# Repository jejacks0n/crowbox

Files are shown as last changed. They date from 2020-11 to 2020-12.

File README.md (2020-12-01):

CrowBox (UNOFFICIAL REPO)
=========================

This is an unofficial repository of resources for the [CrowBox project](http://www.thecrowbox.com). IT IS NOT OFFICIAL, and reflects only the changes I've made. If you want, check out the `original` branch for the original resources as they were when this repo was created.

## About the Project

The CrowBox is an experimentation platform designed to autonomously train corvids (the family of birds crows belong to). So far we’ve trained captive crows to deposit dropped coins they found on the ground in exchange for peanuts. The next step is to work with wild corvids and see if we can get them to learn to use the box, then to optimize the training protocol to see how quickly they can learn from each other.

That's where you come in. Different corvids learn at different speeds and in different ways, and the only way to figure out the best way to teach them is through experimentation. The more people try different things the faster we'll all figure out how to work cooperatively with crows.

Once we’ve got the system optimized for teaching coin collection we can move to seeing how flexibly they can learn *other* tasks, like collecting garbage, sorting through discarded electronics, or maybe even search and rescue.

The idea isn't to get rich off found coins - we want to change the world through learning how to cooperate with other species.

## How it Works

Based on established Skinnerian training principles, the action of the device is divided into four stages:

- Stage 1: Discovery and free feeding
- Stage 2: Food available on landing
- Stage 3: Food available on coin deposit, training coins provided
- Stage 4: Food available on coin deposit

So far the CrowBox project has been shown to work with captive crows. Now we're releasing the open sourced designs of the new CrowBox so anyone can try it with their own wild corvid populations!

## Project Objectives

Nobody's going to get rich training corvids, but we might just change how humanity engages with other species.

The CrowBox is an appliance for experimentation in training and interacting with these birds: it's our goal to get people to think differently about how humanity is already training animals like crows, rats, racoons, deer, and other animals that live near us.

Right now we're teaching them to survive as parasites; what would happen if we could find mutually beneficial working relationships instead?

#### As Seen on TED

Watch the [TED Talk](https://www.ted.com/talks/joshua_klein_a_thought_experiment_on_the_intelligence_of_crows).

"Hacker and author [Joshua Klein](https://www.josh.is) is fascinated by crows. After a long amateur study of corvid behavior, he's come up with an elegant machine that may form a new bond between animal and human."

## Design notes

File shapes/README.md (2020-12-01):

CrowBox Shape Files
===================

The SVG shape files here are intended to be used with a laser cutting provider like [Ponoko](https://www.ponoko.com) or to be laser cut at a local maker shop or similar. They're designed to be cut on sheets of 790mm x 384mm (31.1” x 15.1”) acrylic with a thickness of 3mm, and .5mm styrene.

Once you have the housing parts, check out our YouTube Channel for step-by-step assembly videos.

## Ponoku Specific Instructions

You should only need to upload three files total. The transparent acrylic shapes comes in a single or double layout. You can use the double layout to order two sheets of color acrylic and a single sheet of transparent acrylic to build two boxes.

- [color acrylic](https://raw.githubusercontent.com/jejacks0n/crowbox/shapes-3.0/shapes/crowbox_v3_r1_color_acrylic.svg)
- [transparent acrylic (single layout)](https://raw.githubusercontent.com/jejacks0n/crowbox/shapes-3.0/shapes/crowbox_v3_r1_transparent_acrylic_single.svg) or [(double layout)](https://raw.githubusercontent.com/jejacks0n/crowbox/shapes-3.0/shapes/crowbox_v3_r1_transparent_acrylic_double.svg)
- [styrene](https://raw.githubusercontent.com/jejacks0n/crowbox/shapes-3.0/shapes/crowbox_v3_r1_styrene.svg)

<small>Right click links and "Save as..." to download.</small>

When you select the designs and add them to your cart, you're welcome to select whichever color acrylic you'd like. Some of the matte finishes are nice, and it's important to understand and consider that color may play a role in the success of your CrowBox deployment, as crows (and other birds) have unique color vision.

- [Article: Birds Can See a 'Colour' Humans Can't. Now Scientists Have Revealed This Hidden World](https://www.sciencealert.com/birds-can-see-uv-light-now-scientists-can-show-us-what-that-looks-like)
- [Article: Crows remember colours for a year: Japanese study](https://phys.org/news/2011-12-crows-colours-year-japanese.html)
- [Article: Can't crows see yellow?](http://www.gaiapress.com/en/article/525.html)

Note that Ponoko shipping charges make up a big chunk of the final cost of a single set of parts - it's much more price-effective if you and a friend order your sets of parts together. Huge thanks to Danita Craft for pulling these together; see [this thread](https://groups.google.com/g/crowboxkit/c/9xb9-OHnaKQ/m/a6WmhurxAQAJ?pli=1) for more info.

**Disclaimer:** _We have bought several sets of CrowBox parts from Ponoko in order to verify their quality and accuracy. We have had good customer service experiences with them, as well. For these reasons, we're happy to recommend Ponoko as a place for you to buy your parts. Ponoko charges fees for materials, manufacturing services, and shipping but we have no financial interest or affiliation with them. We receive no money when parts are bought at Ponoko - we're just making a service recommendation._

If you'd like to consider other online laser-cutting services, you can download the housing geometry source files from here and submit them to a service of your choosing.

## Source File

The source `.afdesign` file is provided to make refinements or adjustments of your own easier. The source file has been generated using [Affinity Designer](https://affinity.serif.com/en-us/designer), which is a great application and available for a 7 day trial. The trial may be long enough for you to make the desired changes and export new SVG files. The provided SVG files are optimized to reduce multiple passes on laser cutting.

When you export SVGs it's recommended to run them through [ImageOptim](https://imageoptim.com/mac), which helps clean up a lot of things, especially some pesky width/height attributes that can confuse Ponoko or other laser cutters.

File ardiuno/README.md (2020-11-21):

CrowBox Software (CrOS)
=======================

The programmable computer brain that controls the CrowBox is the Arduino UNO microcontroller board.

We'll go through the steps to download the source code for the CrOS software and get it uploaded to an Arduino UNO board, which can then be used to control your CrowBox.

The CrOS software is fully open-source and we encourage you to make changes and improvements to the code and the machine's training protocol.

The Arduino is an extremely popular platform for makers and experimental electronics worldwide. This means that there are a great deal of resources available to help you learn more about the Arduino hardware, the Arduino IDE software, and how to program and modify programs for these great little boards.

If you run into trouble following the instructions on this page, feel free to open an issue, or check out one of these resources for more information:

- [Getting Started with Arduino](https://www.arduino.cc/en/Guide)
- [Arduino UNO Guide](https://www.arduino.cc/en/Guide/ArduinoUno)
- [CrowBox Google Group](http://groups.google.com/group/CrowBoxKit)

### Table of contents

- [Step 1: Download and Install the Arduino IDE Software](#step-1-download-and-install-the-arduino-ide-software)
- [Step 2: Download and Extract the CrOS Software](#step-2-download-and-extract-the-cros-software)
- [Step 3: Load CrOS Software into the Arduino IDE](#step-3-load-cros-software-into-the-arduino-ide)
- [Step 4: Connect the Arduino UNO Board](#step-4-connect-the-arduino-uno-board)
- [Step 5: Upload the CrOS Software to the Arduino UNO Board](#step-5-upload-cros-software-to-arduino-uno-board)

## Step 1: Download and Install the Arduino IDE Software

To install the CrOS Software onto your Arduino UNO microcontroller board, you'll need a computer, a USB (A to B) cable, and the Arduino IDE software, which is available for free download. IDE stands for Integrated Development Environment, but that's not an important detail right now.

Let's get started! First, follow the official instructions at the Arduino website to download and install the version of the Arduino IDE software that matches your computer's operating system:

- [Windows](https://www.arduino.cc/en/Guide/Windows)
- [Mac OSX](https://www.arduino.cc/en/Guide/MacOSX)
- [Linux](https://www.arduino.cc/en/Guide/Linux)

## Step 2: Download and Extract the CrOS Software

In order to get your CrowBox functional, you'll need to download our CrOS software and install it on your Arduino UNO board.

Download the [latest version of the CrOS software].

After you've downloaded this file you should extract the archive, which you can do by double-click the .zip file you've downloaded.

The archive should create a folder named cros which contains the CrOS source code files, which have extensions like .h, .cpp, and a file named cros.ino.

## Step 3: Load CrOS Software into the Arduino IDE

Launch the Arduino IDE software that you downloaded and installed in the previous steps.

From the Arduino menu, select FILE → OPEN. In the file dialog window that appears, navigate to the 'cros_source' folder from step three and select the file named cros.ino then click Open.

The CrOS project files will be loaded and you will see some tabs containing filenames that begin with 'cros'. You can click through these tabs to view the various source code files, or just ignore them if you're not interested.

It's possible that at some point a window will appear near the bottom of the Arduino IDE which says "Updates are available for some of your boards and libraries". It's a good idea to accept these updates, but you may also click the `X` to dismiss this message and ignore the updates.

## Step 4: Connect the Arduino UNO Board

Plug the 'B' end (The big square end) of your USB A to B cable into the square USB socket on your Arduino UNO board. Plug the other end of the USB cable into a free USB port on your computer.

Allow a moment for your operating system to detect the new device. On Windows operating systems, drivers may begin to install. If so, allow this process to finish before proceeding.

In the Arduino IDE menu, select TOOLS → BOARD → ARDUINO/GENUINO UNO.

The details of the next step depend on your operating system:

### Windows

In the Arduino IDE menu, select TOOLS → PORT → and then look for a COM port numbered 3 or higher which is also labeled (Arduino/Genuino Uno) and select it.

Examples: COM6 (Arduino/Genuino Uno) or COM3 (Arduino/Genuino Uno)

### Mac OSX

In the Arduino IDE menu, select TOOLS → PORT → and then select the port named starting with /dev/tty.usbmodem or /dev/tty.usbserial. The port name will probably end with an unusual alphanumeric string.

### Linux

We have no instructions for this step at present! If you are familiar with the Arduino IDE on Linux, please contribute to this section.

## Step 5: Upload CrOS Software to Arduino UNO Board

At the top left of the Arduino IDE window you'll see two round buttons. Locate the round button with an arrow facing to the right. This is the Upload button.

Click the Upload button.

The CrOS software will compile on your computer and then be uploaded to the Arduino UNO board which you've connected to your computer with the USB cable. If you receive an error message, the best place to turn for help is the issues, or the [CrowBox Google Group](http://groups.google.com/group/CrowBoxKit)

Once the upload is complete, leave the Arduino UNO board connected to your computer for 30 seconds before disconnecting the USB cable.

Your CrowBox software should now be ready to operate!

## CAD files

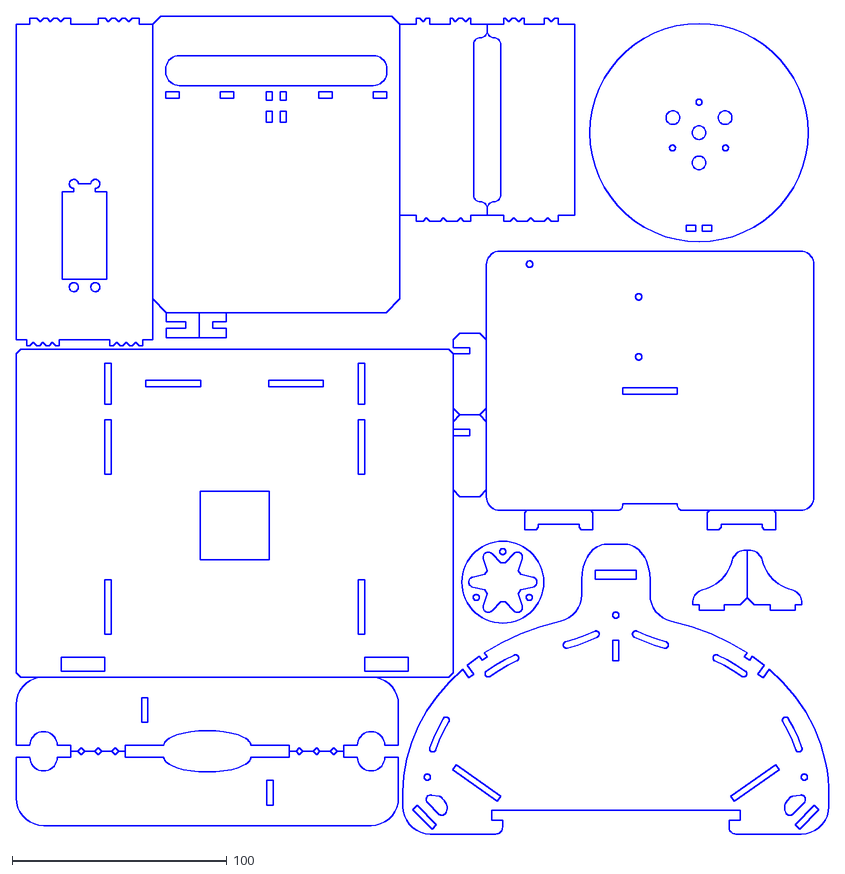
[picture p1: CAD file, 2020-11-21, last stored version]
shapes/crowbox_v2_r2_transparent.dxf
378.0 x 380.6

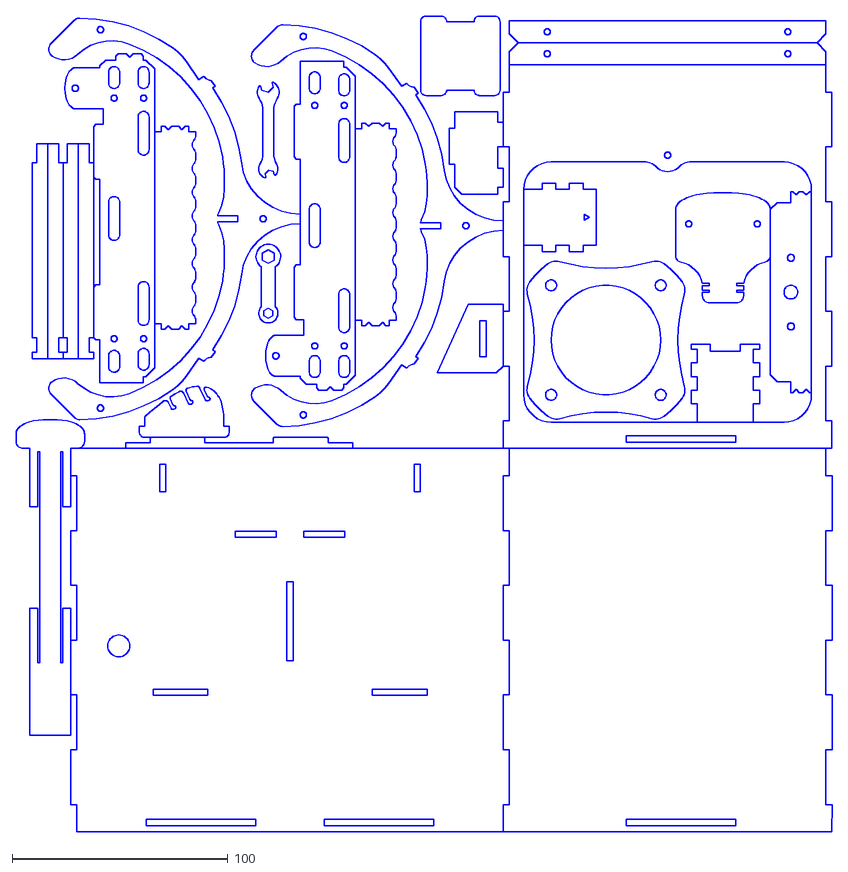
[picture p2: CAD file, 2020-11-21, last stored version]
shapes/source/crowbox_v2_r2_dark.dxf
378.2 x 378.1

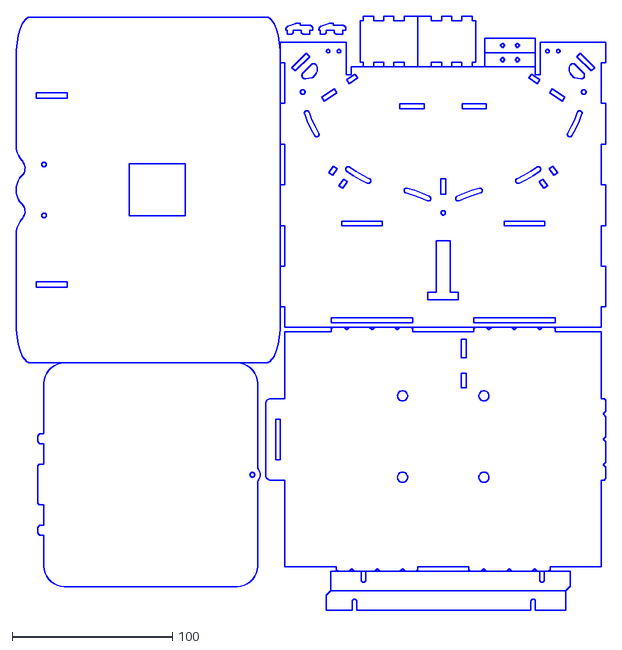
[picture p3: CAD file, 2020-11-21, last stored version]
shapes/crowbox_v2_r2_light.dxf
368.3 x 370.8

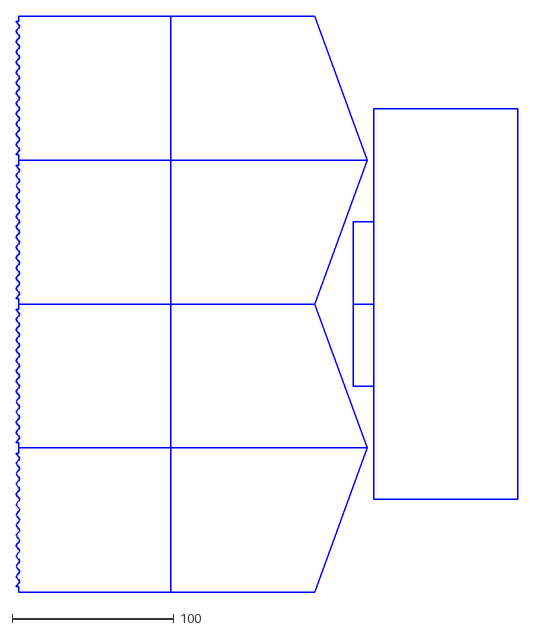
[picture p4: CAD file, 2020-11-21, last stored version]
shapes/crowbox_v2_r2_styrene.dxf
309.7 x 355.6

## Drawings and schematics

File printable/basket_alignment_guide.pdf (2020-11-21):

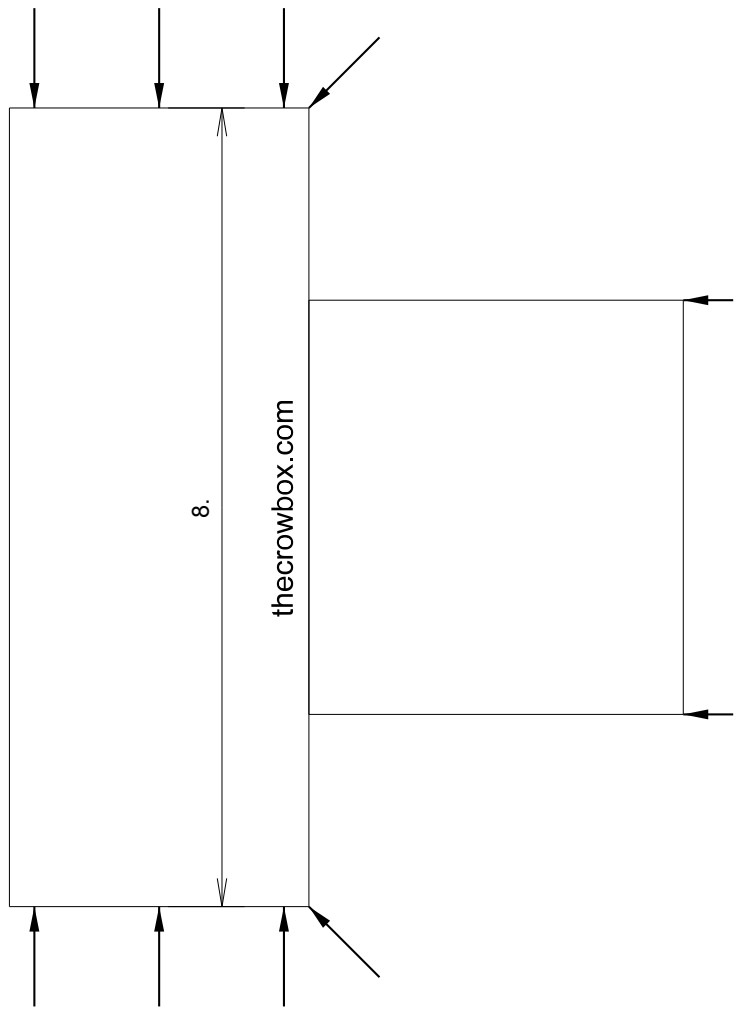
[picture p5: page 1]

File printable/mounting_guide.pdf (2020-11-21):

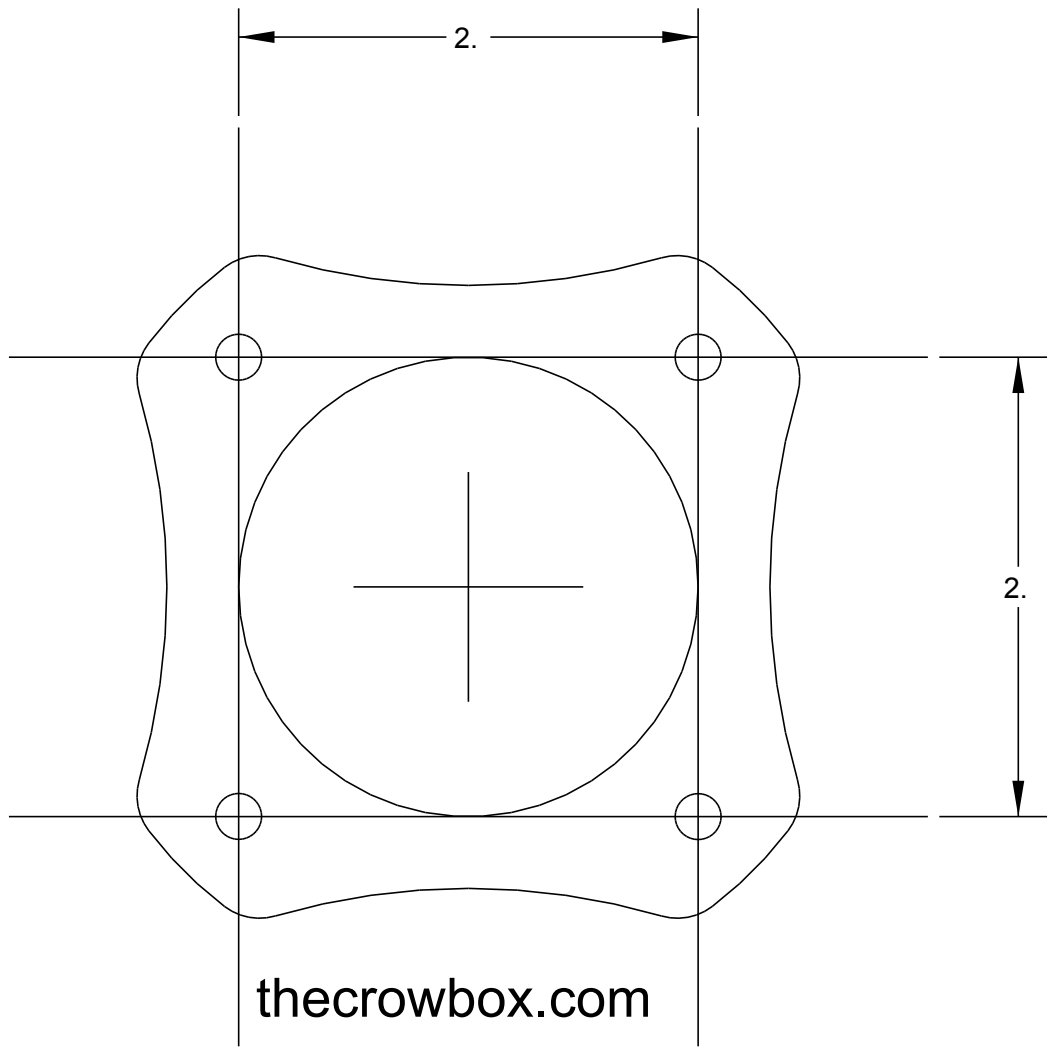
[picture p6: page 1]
thecrowbox.com

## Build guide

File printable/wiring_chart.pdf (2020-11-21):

Wiring Chart
Companion to CrowBox assembly videos- See Official CrowBox YouTube channel September 6, 2018

www.thecrowbox.com
Components Installed to Breadboard
Training Button | Straddle rows 7 to 9, align to far right breadboard edge
Terminal block | Insert at bottom right of breadboard

Breadboard/Arduino Wiring
GND Jumper* | Breadboard E-17 | Breadboard F-17
5V Jumper** | Breadboard E-15 | Breadboard F-15
Perch Rail | Breadboard F-1 | UNO Pin 2
Perch Rail | Breadboard F-2 | Breadboard D-17
Training | Breadboard F-7 | UNO Pin 4
Training | Breadboard F-9 | Breadboard G-17
UNO 5V** | Breadboard A-15 | UNO ‘5V’
UNO GND* | Breadboard A-17 | UNO ‘GND’

* We suggest BROWN wire for this connection
** We suggest RED wire for this connection

Connections From Crowbox
Servo | BROWN - Breadboard B-17 RED - Breadboard B-15 ORANGE - UNO 9 | *Be sure to use dupont wires that match servo wire colors. See video for details.
Coin Sensor | Either wire from sensor | UNO Pin 3
Coin Sensor | Either wire from sensor | UNO ‘GND’
Perch | Pair from either limit switch | Column G1
Perch | Pair from either limit switch | Column H1

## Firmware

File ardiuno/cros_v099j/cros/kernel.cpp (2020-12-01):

//=============================================================================
// The CrowBoxOS (CrOS)
//
// Unofficial Version ~0.99j - December 2020
//
// http://www.thecrowbox.com
//=============================================================================
// Except where otherwise noted, this work is licensed under a Creative Commons
// Attribution-ShareAlike 4.0 International License.
//=============================================================================
#include <EEPROM.h>
#include "kernel.h"

namespace CrOS {
  void Log(const char *message) {
#if defined(CROS_SERIAL_BAUD_RATE)
    if (!Serial.available()) Serial.begin(CROS_SERIAL_BAUD_RATE);

    Serial.print("CrOS: ");
    Serial.println(message);
#endif // CROS_SERIAL_BAUD_RATE
  }

  void InterruptHandler() {
    const unsigned long uptime = millis();
    if (lastInterruptUptime > uptime - 1000) return;

    lastInterruptUptime = uptime;
    pendingInterruptEvent = true;
  }

  void Shutdown(const char *message) {
    Log(message);
    Log("Shutting down...");
    while (true) {};
  }

  Kernel::Kernel() {}

  void Kernel::Register(void (*handler)(event eventType)) {
    m_eventHandlers[++m_eventHandlersLen] = handler;
  }

  void Kernel::Boot() {
    Log("Booting up...");

    // Setup the pin modes.
    pinMode(LED_BUILTIN, OUTPUT);
    pinMode(CROS_INPUT_PIN_PERCH, INPUT_PULLUP);
    pinMode(CROS_INPUT_PIN_COIN, INPUT_PULLUP);
    pinMode(CROS_INPUT_PIN_TRAINING_PHASE, INPUT_PULLUP);

    // Initialize the servo.
    Log("Initializing basket servo...");
    SetLidPosition(50);
    delay(800);
    SetLidPosition(0);

    // Load the training phase from the EEPROM or default it.
    currentTrainingPhase = EEPROM.read(CROS_EEPROM_ADDRESS_TRAINING_PHASE);
    if (currentTrainingPhase < 1 || currentTrainingPhase > 4) currentTrainingPhase = 1;

    char message[100];
    sprintf(message, "Initializing training phase %i.", currentTrainingPhase);
    Log(message);

    // Register the interrupt.
    attachInterrupt(digitalPinToInterrupt(CROS_INPUT_PIN_COIN), InterruptHandler, FALLING);
    Log("Coin interrupt registered.");

    // Blink the LED to indicate the current training phase.
    BlinkLED(currentTrainingPhase);

    // Close the lid if we should.
    if (currentTrainingPhase != 1) m_initCloseBasketAt = 5000;
  }

  void Kernel::Loop() {
    const unsigned long uptime = millis();

    if (pendingInterruptEvent) {
      // Handle coin events.
      ProcessEvent(COIN_ACTIVATED);

      pendingInterruptEvent = false;
    } else {
      // Handle perch events.
      const bool perchActive = InputFrom(CROS_INPUT_PIN_PERCH);

      if (!m_perchActive && perchActive) ProcessEvent(PERCH_ACTIVATED);
      else if (m_perchActive && !perchActive) ProcessEvent(PERCH_DEACTIVATED);

      m_perchActive = perchActive;
    }

    // Handle the training phase cycle button.
    if (InputFrom(CROS_INPUT_PIN_TRAINING_PHASE, true)) NextTrainingPhase();

    // Close the lid in steps.
    if (m_initCloseBasketAt > 0 && m_initCloseBasketAt < uptime) {
      SetLidPosition(m_lidPosition + 10);
      if (m_lidPosition >= 100) m_initCloseBasketAt = 0;
      else m_initCloseBasketAt = uptime + CROS_BASKET_CLOSE_STEP_DURATION;
    }

    // Detach the servo if we need to.
    if (m_servoDetachAtUptime > 0 && m_servoDetachAtUptime < uptime) {
      m_servo.detach();
      m_servoDetachAtUptime = 0;
    }

    unsigned long duration = millis() - uptime;
    if (duration < 20) delay(20 - duration);
  }

  void Kernel::Reward() {
    SetLidPosition(0);
    m_initCloseBasketAt = millis() + CROS_BASKET_REWARD_DURATION;
  };

  void Kernel::NextTrainingPhase() {
    if (++currentTrainingPhase > 4) currentTrainingPhase = 1;

    // Save the training phase in EEPROM.
    EEPROM.write(CROS_EEPROM_ADDRESS_TRAINING_PHASE, currentTrainingPhase);

    // Reset the device.
    delay(250);
    pinMode(CROS_OUTPUT_PIN_RESET, OUTPUT);
  }

  void Kernel::ProcessEvent(event eventType) {
    switch (eventType) {
      case COIN_ACTIVATED:
        Log("Event: COIN_ACTIVATED");
        if (currentTrainingPhase > 2) Reward();
        break;
      case PERCH_ACTIVATED:
        Log("Event: PERCH_ACTIVATED");
        if (currentTrainingPhase == 2) Reward();
        break;
      case PERCH_DEACTIVATED:
        Log("Event: PERCH_DEACTIVATED");
        break;
    }
  
    for (unsigned char i = 0; i <= m_eventHandlersLen; ++i) m_eventHandlers[i](eventType);
  }  

  bool Kernel::InputFrom(const unsigned char pin, const bool waitForRelease = false) {
    if (digitalRead(pin) != LOW) return false;

    if (waitForRelease) while (digitalRead(pin) == LOW) delay(50);
    return true;
  }

  void Kernel::SetLidPosition(unsigned char percent) {
    if (percent > 100) percent = 100;

    m_servo.attach(CROS_OUTPUT_PIN_SERVO);
    m_servo.write(percent / 100.0 * 179);

    m_lidPosition = percent;
    m_servoDetachAtUptime = millis() + 2000;
  }

  void Kernel::BlinkLED(const unsigned char numTimes = 1) {
    for (unsigned char i = 0; i < numTimes; ++i) {
      digitalWrite(LED_BUILTIN, HIGH);
      delay(250);

      digitalWrite(LED_BUILTIN, LOW);
      delay(250);
    }
  }
}

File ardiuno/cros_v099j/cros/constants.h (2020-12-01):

//=============================================================================
// The CrowBoxOS (CrOS)
//
// Unofficial Version ~0.99j - December 2020
//
// http://www.thecrowbox.com
//=============================================================================
// Except where otherwise noted, this work is licensed under a Creative Commons
// Attribution-ShareAlike 4.0 International License.
//=============================================================================
#ifndef CROS_CONSTANTS_H
#define CROS_CONSTANTS_H

// Settings for serial communications. This is used for debug text-based error
// and status messages in the serial monitor / console.
//
// CROS_SERIAL_BAUD_RATE should be #undef when compiling for a CrowBox that's
// going to be deployed -- for performance and optimization reasons.
#undef CROS_SERIAL_BAUD_RATE
//#define CROS_SERIAL_BAUD_RATE 9600

// Pin apportioning. The following assumes an Arduino board, and these may need
// to be changed when porting this code to run on another board type, or when
// changing wiring.
//
// The PERCH and COIN pins must support interrupts.
#define CROS_INPUT_PIN_PERCH 2
#define CROS_INPUT_PIN_COIN 3
#define CROS_INPUT_PIN_TRAINING_PHASE 4
#define CROS_OUTPUT_PIN_SERVO 9
#define CROS_OUTPUT_PIN_RESET 10

// Constants used to store the CrOS data in the EEPROM so that it will be
// remembered on restarts.
#define CROS_EEPROM_ADDRESS_TRAINING_PHASE 0

// Basket and servo behavior. These define an important safety feature which
// closes the lid slowly in a series of small steps. This ensures visitors have
// plenty of time before there's any danger of getting one of their parts
// caught.
//
// Think carefully before changing these.
#define CROS_BASKET_REWARD_DURATION 15000
#define CROS_BASKET_CLOSE_STEP_DURATION 1500

// WiFi support is an optional configuration. If you have a Arduino Uno WiFi
// Rev 2 you might want to configure and turn these features on.
#undef CROS_NETWORK_SSID
//#define CROS_NETWORK_SSID ""
//#define CROS_NETWORK_PASS ""
//#define CROS_API_HOST "" // this would be "www.corvusludus.live"
//#define CROS_API_TOKEN ""
//#define CROS_API_REQUEST "HEAD /log_event?type=%i&token=%s HTTP/1.1\nHost: %s\nConnection: close\n\n"
#define CROS_API_REQUEST "HEAD /event?type=%i&token=%s HTTP/1.1\r\nHost: %s\r\nConnection: close\r\nUser-Agent: CrOS/0.99j"

#endif // CROS_CONSTANTS_H

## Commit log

2020-11-21 3.0 shapes with affinity designer and eps sources
    [crowbox_v2_r2_dark.dxf, crowbox_v2_r2_light.dxf, crowbox_v2_r2_styrene.dxf, crowbox_v2_r2_transparent.dxf]
2020-12-01 Fix basket shoulder and electronics enclosure
